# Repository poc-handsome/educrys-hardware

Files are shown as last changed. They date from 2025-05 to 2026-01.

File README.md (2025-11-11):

# educrys-hardware


Subfolders contain the documentation for [mechanical](/mechanical-design) (TODO) and [electronic](/electronic-design) (TODO) design of EduCrys setup for the users who want to build or adapt it by themselves.

The sections below provide information for users who have received a ready-to-use setup.

## Packing

While most electronic components of EduCrys are enclosed in a robust metallic box, many sensors and other parts need careful packing to avoid damage during transport. The pictures below show an example of such packing. The final package has dimensions of 60x41x23 cm and weight of 13.3 kg.

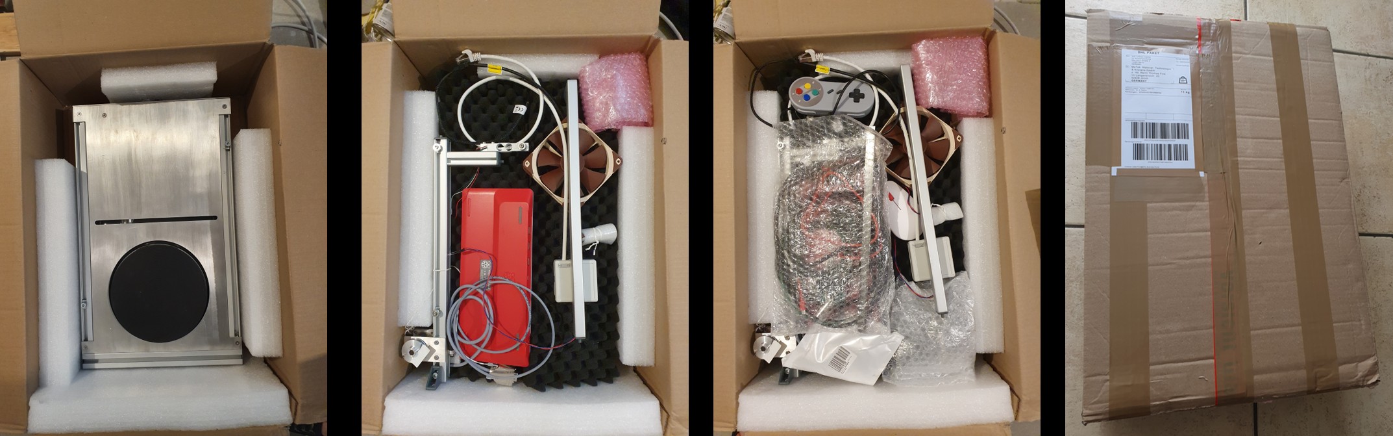
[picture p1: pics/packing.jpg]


## Transport without packing

If the EduCrys setup is transported in the partly-assembled state, the following safety measures are recommended:

- Disconnect the rotation motor, detach the seed holder, wind the pulling wire on the main pulley and fix it with a tape
- Disconnect the camera and detach it from the magic arm
- Tape the crucible and camera cable to the main body to prevent motion
- Pack the seed holder and camera separately

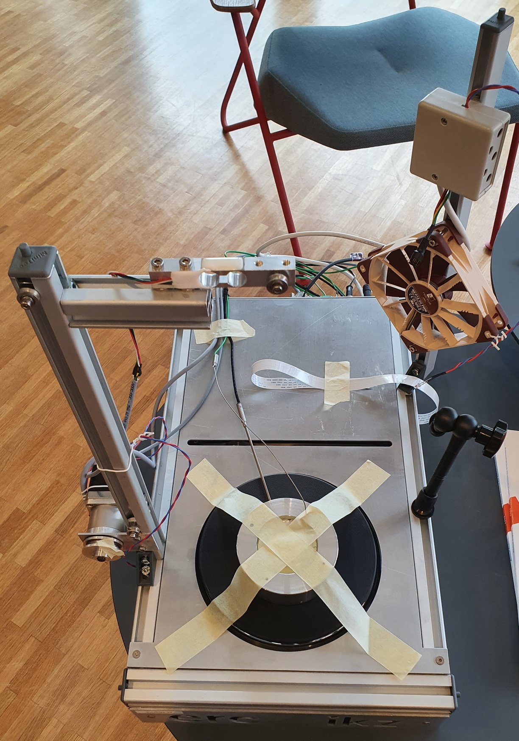
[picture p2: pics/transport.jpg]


## List of components

### Main components

- Main body with all connectors detached, except the camera cable, which is taped on the right wall. Two M6 screws are left in the profiles on both sides.
- Main stand with the pulling motor and weight cell. The pulling wire is wound and taped on the motor roll.
- Second stand with the fan and the small sensor box. The infrared sensor and LED should be protected with bubble wrap.
- Seed holder with a rotation motor in a bubble wrap bag. Small S-shaped hook to attach the seed holder to the pulling wire.
- Aluminum crucible with solid tin (99.9%), in a bubble wrap bag, should not move around in the transport box.

### Sensors and cables

- Raspberry Pi camera with a cover, attached to a magic arm, all inside a bubble wrap
- 1x PT100 and 2x thermocouple sensors with about 1.5 m wire length
- Raspberry Pi keyboard incl. USB cable and mouse, gamepad
- HDMI monitor cable, power cable

### Tools

- 30 cm metallic ruler
- Small spoon and small metal blow to be used when removing oxide layer
- 3 Inbus keys for seed holder, for opening main body, and for mounting both vertical profiles
- Nylon wire, which can be used temporarily if the steel wire of the seed holder breaks
- Warning sign for hot surfaces

### Raw material

- About 1 mm thick tin crystal, which can be used as seed
- About 1 mm thick copper wire, which can be used as seed
- (Tin pellets with 99.9% purity)

### Not included
- Protective glasses when working close to the crucible. **The hot liquid metal may splash if something falls into the melt!**
- Protective gloves when touching the hot crucible, for example, to adjust its position.
- Monitor
- Power strip

## Assembling the setup

### Mechanical

- Place the main body on a table with the logo on the front
- Attach the main stand on the left profile with a M6 screw, close to the front. Connect the motor and weight cell cables.
- Attach the fan stand on the right profile with a M6 screw, close to the back. Connect the fan and sensor cables.
- Guide the pulling wire over 3 pulleys from the pulling motor to the weight cell. Insert a hook in the loop at the wire end. Keep the wire tightened, otherwise it will unwind itself from the pulley on the motor axis.
- Hang the seed holder on the hook. The tilt of the seed holder should remain adjustable in two perpendicular directions.
- Attach the cable with two pins to the rotation motor. The polarity is not important. Keep the free length of this cable sufficient during the motion of the seed holder. This cable prevents the seed holder from rotating, but it should not pull it away from the vertical axis.
- Place the crucible on the hotplate. Check that the seed holder is in the middle of the crucible. Adjust the main stand position if necessary.

### Sensors and cables

- Attach the magic arm with camera on the right profile, close to the front. Carefully pull out the camera cable from the slit in the right wall. Insert the cable end into the connector at the back of the camera with the conducting pins towards the board. Push the black connector part upwards to fix the cable.
- Insert the PT100 sensor in a horizontal borehole and one thermocouple in a vertical borehole of the crucible. Both sensor cables should be bound together to prevent the PT100 sliding out of the hole. **This would lead to strong overheating of the crucible during temperature-controlled heating!**
- The second thermocouple could be used to measure ambient air, melt, or some parts inside the main body.
- Connect the keyboard with the red USB cable to the socket in the right wall. Connect the mouse and the gamepad to the keyboard. The USB ports in the keyboard can be also used to attach USB flash memory for data transfer.
- Connect a monitor to the HDMI socket in the right wall.
- Attach the power cable at the back of the main body. **Raspberry Pi starts as soon as power is connected! Always use the shutdown function in the Menu before disconnecting the power to avoid data loss.**
- If necessary, a network cable can be attached directly to the Raspberry Pi board through an opening in the back wall. Remove the screws and carefully pull the back wall for about 5 cm to access Raspberry Pi. **The network socket in the back wall can be only used for the sensor box.**

### Clock 

- Check the system clock after the log in. Newer EduCrys setups have a hardware clock with battery backup, while others rely on synchronization over network.
- The following steps are required to install an external hardware clock, see also [raspberry-pi-geek.de](https://www.raspberry-pi-geek.de/ausgaben/rpg/2015/03/echtzeituhr-modul-ds3231-sorgt-fuer-genaue-zeitangaben/2/) 
  - Update system time: `sudo date -s "19 May 2025 18:00:00" `
  - Attach the hardware clock to the I2C bus and find the address (e.g. 68): `sudo i2cdetect -y 1`
  - Configure the system to use the hardware clock (use the address from above) and add this line also to /etc/rc.local: `echo ds3231 0x68 | sudo tee /sys/class/i2c-adapter/i2c-1/new_device`
  - Synchronize the hardware clock with system time: `sudo hwclock -w`
  - Disable synchronization over network: `sudo update-rc.d ntp disable`   `sudo update-rc.d fake-hwclock disable`   `sudo timedatectl set-ntp false`

The final setup should look like this.



## Acknowledgements

[This project](https://poc-handsome.github.io/) has received funding from the European Research Council (ERC) under the 
European Union’s Horizon Europe framework programme for research and innovation (grant agreement No. 101122970).



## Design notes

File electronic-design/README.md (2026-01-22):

## E01 PCB

### Layout of the PCB

Design files for KiCad (8.0.0) are here: [KiCad](https://github.com/poc-handsome/educrys-hardware/tree/main/electronic-design/E01/KiCad)

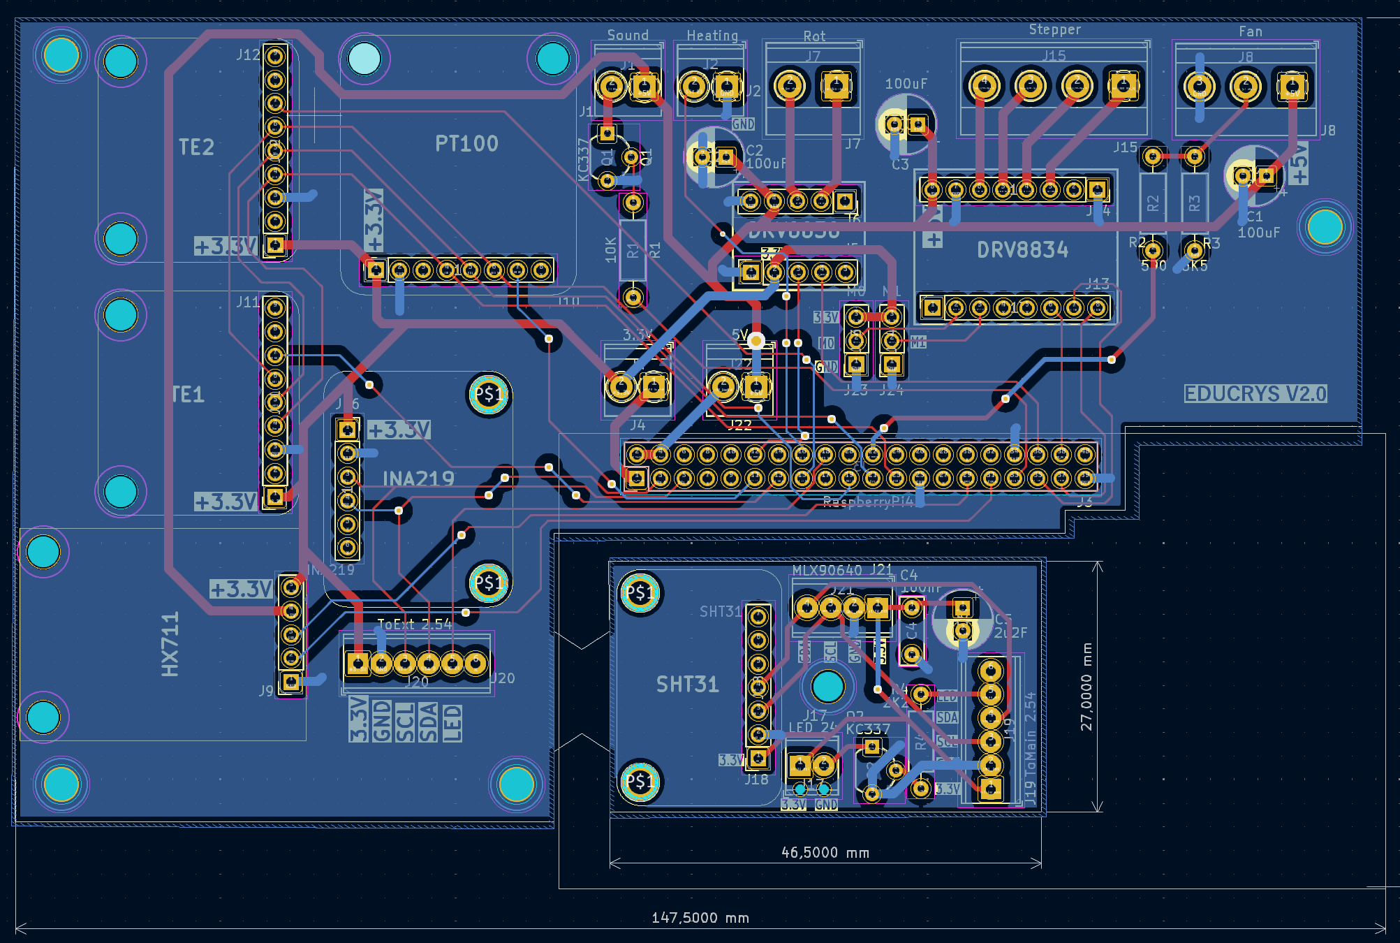
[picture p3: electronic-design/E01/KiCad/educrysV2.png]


The following improvements have not been implemented yet:
- Separate pin header for the clock module
- Larger screw terminal for the connection between main PCB and sensor PCB
- Avoid risk of short circuit when soldering capacitors

### Soldering

Main PCB with soldered parts, top and bottom views:

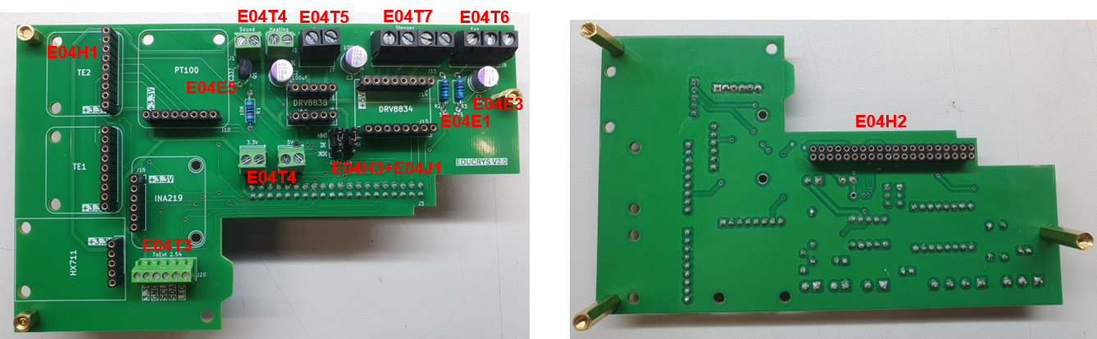
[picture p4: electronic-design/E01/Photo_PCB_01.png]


Sensor PCB with soldered parts, top and bottom views:

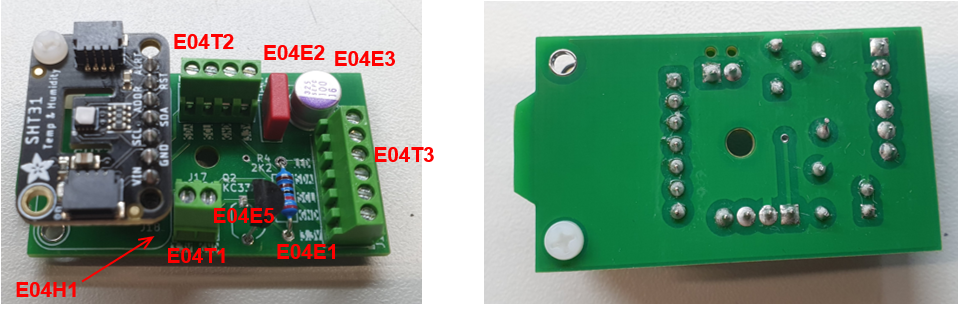
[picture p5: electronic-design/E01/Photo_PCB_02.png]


Remarks:
- The connection between the main board and sensor board must be cut 
- For all screw terminals the holes are oriented to the rim of the board 
- A small 2 mm gap should be left between the 100 uF capacitor to avoid short circuit 
- Resitor values are not printed correctly on the board, use closes E12 values
- All flux residues should be cleaned from both board sides, e.g. using Kontaktchemie LR

### Modules

PCB after mounting the modules:

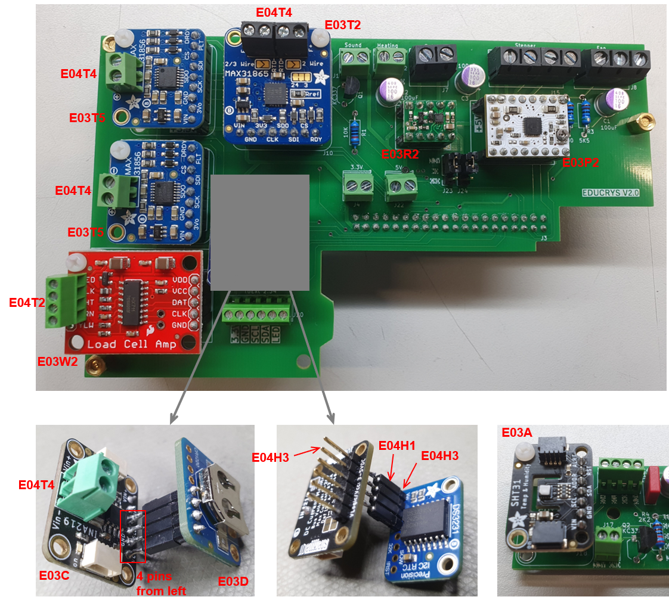
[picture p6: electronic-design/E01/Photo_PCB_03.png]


Remarks:

- First solder pin headers [E04H3] on the bottom of all modules [E03T2 etc.]. Make short breaks to avoid overheating the chip
- Solder screw terminals on the top of modules [E03T5, E03T2, E03W2, E03C]. The holes are oriented to the center of the board for [E03T5, E03W2] and to the rim of the board for [E03T2, E03C]
- Solder a female header on the top of the module [E03C] (4 pins on the left) and connect the module [E03D] there
- All flux residues should be cleaned from both board sides, e.g. using Kontaktchemie LR
- The modules will be fastened later to the PCB with a 10 mm spacer and two M2.5 screws. M3 screws are too big!

## E02 Wiring diagram

Schematic of the connections using the parts given below:

(pic)

Photo of the final wiring

(pic)

Remarks:

## E03 Devices: sensors, actuators

Prices are given per one piece in EUR incl. VAT. 

| Part  | Description                             | Use               | Price | Vendor/Link              | Datasheet | 
|-------|-----------------------------------------|-------------------|-------|--------------------------|-----------|
| E03H  | Hotplate, Severin KP 1092               | Crucible heating  | 27.99 | [Conrad/704233](https://www.conrad.de/de/p/severin-kp-1092-1092-kochplatte-704233.html?searchType=SearchRedirect)       |           |
| E03P1 | Stepper, Nema-17 1:20                   | Crystal pulling   | 56.90 | [Conrad/2355877](https://www.conrad.de/de/p/joy-it-schrittmotor-nema17-07gm-0-44-nm-1-68-a-wellen-durchmesser-8-mm-2355877.html?searchType=SearchRedirect)        |           |
| E03P2 | Motor driver IC, DRV8834                | Stepper motor     | 8.24  | [Exptech/80-2134](https://exp-tech.de/products/pololu-drv8834-low-voltage-stepper-motor-driver-carrier)     |           |
| E03R1 | DC motor 1000:1                         | Seed rotation     | 12.95 | [Conrad/1289388](https://www.conrad.de/de/p/sol-expert-g1000-micro-getriebemotor-g-1000-metallzahnraeder-1-1000-2-18-u-min-1289388.html?searchType=SearchRedirect)      |           |
| E03R2 | Motor driver IC, DRV8838                | DC motor          | 4.10  | [Exptech/80-2990](https://exp-tech.de/products/pololu-drv8838-single-brushed-dc-motor-driver-carrier)      |           |
| E03F1 | Fan, 120 mm, 5V                         | Crystal cooling   | 35.61 | [Conrad/816459971](https://www.conrad.de/de/p/noctua-nf-f12-5v-pwm-fan-1-pack-brun-120-mm5-v-pwm-0-75-w-0-15-a-93-4-816459971.html?searchType=SearchRedirect)    |           |
| E03W1 | Weight cell, 1 kg                       | Crystal weight    | 39.37 | [Conrad/2104290](https://www.conrad.de/de/p/sauter-ck-1-0p1-ck-1-0p1-messzelle-ck-p1-4-2104290.html?searchType=SearchRedirect)      |           |
| E03W2 | Weight cell driver IC, HX711            | Weight cell       | 9.86  | [Digikey/1568-1436-ND](https://www.digikey.de/de/products/detail/sparkfun-electronics/13879/6202732?s=N4IgTCBcDaIIwFYBsAOAtHALAZiWgcgCIgC6AvkA)     |           |
| E03T1 | Thermal sensor PT100, 3x150 mm, 500 °C  | Temperature sensor | 142.87 | [RS/397-1315](https://de.rs-online.com/web/p/widerstands-temperatursensoren/3971315?searchId=d1256e21-5988-4aaf-8b94-83c79a26ba8f)             |           |
| E03T2 | PT100 driver IC, MAX31865               | Temperature sensor | 12.82 | [Digikey/1528-3328-ND](https://www.digikey.de/de/products/detail/adafruit-industries-llc/3328/6562952)    |           |
| E03T4 | 2x Thermocouple, Type K, 1x250 mm, 750 °C | Temperature sensor | 47.36 | [RS/787-7706](https://de.rs-online.com/web/p/thermoelemente/7877706?searchId=9bbca203-3abb-4fba-a2c3-11345d2f288b)       |           |
| E03T5 | Thermocouple driver IC, MAX31856        | Temperature sensor | 17.98  | [Digikey/1528-1772-ND](https://www.digikey.de/de/products/detail/adafruit-industries-llc/3263/6227009?s=N4IgTCBcDaIIwFYwA4C0cDsGyoHIBEQBdAXyA)    |           |
| E03C  | Current sensor, INA219                  | Motor current     | 8.53   | [Digikey/1528-904-ND](https://www.digikey.de/de/products/detail/adafruit-industries-llc/904/5353628?s=N4IgTCBcDaIIwFYwA4C0BOADAFlQOQBEQBdAXyA)      |           |
| E03A  | Air sensor, SHT31                       | Air temperature, humidity | 11.96 | [Digikey/1528-2857-ND](https://www.digikey.de/de/products/detail/adafruit-industries-llc/2857/5804106?s=N4IgTCBcDaIIYBM4DMBOBXAlgFwAQGUAJAFQGYBGEAXQF8g) |           |
| E03I  | IR sensor, MLX90640                     | Hotplate temperature | 30.28 | [Digikey/MLX90640ESF-BAB-000-TU-ND](https://www.digikey.de/de/products/detail/melexis-technologies-nv/MLX90640ESF-BAB-000-TU/8638464?s=N4IgTCBcDaILIBkAaBOADANgCxoKIGUAxAWgCEBBU4tG4gFQFViA5AERAF0BfIA) |           |
| E03D  | Real time clock, DS3231                 | Raspberry Pi time backup | 15.0  | [Digikey/1528-3013-ND](https://www.digikey.de/de/products/detail/adafruit-industries-llc/3013/5875808) |           |
| E03O1 | RPi camera                              | Optical camera | 51.90 | [Welectron/RP3-102610](https://www.welectron.com/Offizielle-Raspberry-Pi-HQ-Camera)        |           |
| E03O2 | Camera lens 8-50 mm                     | Optical camera | 42.90 | [Welectron/WS9-018245](https://www.welectron.com/Waveshare-18245-8-50mm-Zoom-Lens-for-Pi)        |           |

## E04 Electrical components

Prices are given per one piece in EUR incl. VAT. In some cases SETS with a larger number of parts are given.

| Part  | Description                             | Use               | Price | Vendor/Link              | Datasheet | 
|-------|-----------------------------------------|-------------------|-------|--------------------------|-----------|
| E04S1 | 2x Power socket                         | SSR box           | 4.79  | [Conrad/2484787](https://www.conrad.de/de/p/as-schwabe-45084-einbau-steckdose-grau-2484787.html?searchType=SearchRedirect)  |  |
| E04S2 | Solid state relais                      | SSR box           | 74.52 | [RS/491-4947](https://de.rs-online.com/web/p/halbleiterrelais/4914947)  |  |
| E04R1 | Raspberry Pi 4 B (4 GB)                 |                   | 57.90 | [Welectron/RP1-141400](https://www.welectron.com/Raspberry-Pi-4-B-4-GB)  |  |
| E04R2 | SD card 64GB                            | Raspberry Pi      | 6.9   | [Welectron/SD1-200644](https://www.welectron.com/SanDisk-SDSQUAB-064G-GN6MA-Ultra-microSD-Speicherkarte-64-GB-140-MB-s)  |  |
| E04R3 | Heatsink                                | Raspberry Pi      | 1.3   | [Welectron/409151](https://www.welectron.com/Raspberry-Pi-Kuehlkoerpersatz)  |  |
| E04R4 | Power supply 5V, 3A                     | Raspberry Pi      | 7.5   | [Welectron/408024-012](https://www.welectron.com/Offizielles-Raspberry-Pi-4-Steckernetzteil-USB-C-51V-3A-weiss-EU)  |  |
| E04R5 | Keyboard + mouse                        | Raspberry Pi      | 27.90 | [Welectron/409483-002](https://www.welectron.com/Offizielle-Raspberry-Pi-Tastatur-Maus-Kombination-rot-weiss-DE)  |  |
| E04R6 | Gamepad                                 | Raspberry Pi      | 4.99  | [Conrad/1954771](https://www.conrad.de/de/p/joy-it-gamepad-snes-design-gamepad-raspberry-pi-universal-grau-1954771.html?searchType=SearchRedirect)  |  |
| E04E1 | SET: Metal film resistors               | PCB               | 46.65 | [Reichelt/METALL E 12](https://www.reichelt.de/de/de/shop/produkt/metallschichtwiderstandssortiment_e12-12049)  |  |
| E04E2 | SET: Foil capacitors                    | PCB               | 83.50 | [Reichelt/SORTIMENT 100](https://www.reichelt.de/de/de/shop/produkt/sortimentsbox_folienkondensatoren_rm_5mm-19263)  |  |
| E04E3 | 4x Capacitor 100 uF                     | PCB               | 1.29  | [Conrad/1179727](https://www.conrad.de/de/p/panasonic-16sepc100m-elektrolyt-kondensator-radial-bedrahtet-2-5-mm-100-f-16-v-dc-20-o-x-h-6-3-mm-x-6-mm-1-st-1179727.html)  |  |
| E04E4 | Buzzer                                  | PCB               | 0.99  | [Reichelt/KXG1205C](https://www.reichelt.de/de/de/shop/produkt/indikator_85db_2300_hz_5_v-360852)  |  |
| E04E5 | 2x Transistor KC337                     | PCB               | 0.02  | [Reichelt/BC 337-16](https://www.reichelt.de/de/de/shop/produkt/bipolartransistor_npn_45v_0_8a_0_625w_to-92-4985)  |  |
| E04E6 | White LED                               | Sensor box        | 0.5   | [Conrad/180754](https://www.conrad.de/de/p/nichia-nspw300ds-sel-b2v-w-led-bedrahtet-weiss-rund-3-mm-15000-mcd-20-20-ma-3-2-v-180754.html)  |  |
| E04H1 | 3x Female header precision, 2.54 mm, 1x36 | PCB             | 3.79  | [Conrad/733779-VQ](https://www.conrad.de/de/p/mpe-garry-buchsenleiste-praezision-anzahl-reihen-1-polzahl-je-reihe-36-115-1-036-0-mtf-xs0-1-1-st-733779.html)  |  | 
| E04H2 | 2x Female header precision, 2.54 mm, 2x10 | PCB             | 2.79  | [Conrad/733843-VQ](https://www.conrad.de/de/p/mpe-garry-buchsenleiste-praezision-anzahl-reihen-2-polzahl-je-reihe-10-115-3-020-0-mtf-xs0-1-st-733843.html)  |  |
| E04H3 | 2x Pin header, 2.54 mm, 1x50              | PCB             | 1.79  | [Conrad/734220-VQ](https://www.conrad.de/de/p/mpe-garry-stiftleiste-standard-anzahl-reihen-1-polzahl-je-reihe-50-087-1-050-0-s-xs0-1260-1-st-734220.html)  |  |
| E04T1 | Screw terminal, 2.54 mm, 2p               | PCB             | 0.34  | [Conrad/567588-83](https://www.conrad.de/de/p/ptr-hartmann-50692020021e-schraubklemmblock-0-75-mm-polzahl-2-gruen-1-st-567588.html)  |  |
| E04T2 | Screw terminal, 2.54 mm, 4p               | PCB             | 0.68  | [Conrad/567658-83](https://www.conrad.de/de/p/ptr-hartmann-50692040021e-schraubklemmblock-0-75-mm-polzahl-4-gruen-1-st-567658.html)  |  |
| E04T3 | 2x Screw terminal, 2.54 mm, 6p            | PCB             | 0.96  | [Conrad/567757-83](https://www.conrad.de/de/p/ptr-hartmann-50692060021e-schraubklemmblock-0-75-mm-polzahl-6-gruen-1-st-567757.html)  |  |
| E04T4 | 4x Screw terminal, 3.5 mm, 2p             | PCB             | 0.57  | [Conrad/732295-83](https://www.conrad.de/de/p/ptr-hartmann-50602020021f-schraubklemmblock-1-00-mm-polzahl-2-gruen-1-st-732295.html)  |  |
| E04T5 | Screw terminal, 5.08 mm, 2p               | PCB             | 0.19  | [Conrad/731877-83](https://www.conrad.de/de/p/ptr-hartmann-50500020134g-schraubklemmblock-1-50-mm-polzahl-2-grau-1-st-731877.html)  |  |
| E04T6 | Screw terminal, 5.08 mm, 3p               | PCB             | 0.29  | [Conrad/731891-83](https://www.conrad.de/de/p/ptr-hartmann-50500030134g-schraubklemmblock-1-50-mm-polzahl-3-grau-1-st-731891.html)  |  |
| E04T7 | Screw terminal, 5.08 mm, 4p               | PCB             | 0.39  | [Conrad/731908-83](https://www.conrad.de/de/p/ptr-hartmann-50500040134g-schraubklemmblock-1-50-mm-polzahl-4-grau-1-st-731908.html)  |  |
| E04J1 | 2x Jumper                                 | PCB             | 0.05  | [Reichelt/MPE 149-1-002-F0](https://www.reichelt.de/de/de/shop/produkt/jumper_2_54_mm_geoeffnet_schwarz-119941)  |  |

## E05 Connectors

Prices are given per one piece in EUR incl. VAT. 

| Part  | Description                             | Use               | Price | Vendor/Link              | Datasheet | 
|-------|-----------------------------------------|-------------------|-------|--------------------------|-----------|
| E05P1 | Power socket with fuse, 10A, C14        | Power cable       | 3.29  | [Conrad/2522092](https://www.conrad.de/de/p/tru-components-tc-10088368-kaltgeraete-steckverbinder-c14-stecker-einbau-vertikal-gesamtpolzahl-3-10-a-schwarz-1-st-2522092.html)           |           |
| E05P2 | Fuse (250V, 8A, Flink)                  | Power socken      | 0.18  | [Conrad/524207](https://www.conrad.de/de/p/eska-520-526-520526-feinsicherung-o-x-l-5-mm-x-20-mm-8-a-250-v-flink-f-inhalt-10-st-524207.html?searchType=SearchRedirect)        |           |
| E05M1 | Socket SUB-D-9                          | Motors            | 0.34  | [Conrad/1389963](https://www.conrad.de/de/p/connfly-ds1033-09fbnsiss-ct-d-sub-buchse-180-polzahl-9-loeten-1-st-1389963.html?searchType=SearchRedirect)           |           |
| E05M2 | Jack SUB-D-9                            | Motors            | 1.95  | [Reichelt/MHDTZK 9 S](https://www.reichelt.de/de/de/shop/produkt/d-sub_stecker_9_polig-342366)      |           |
| E05M3 | 2x SUB-D screws                         | Motors            | 0.63  | [Digikey/609-1421-ND](https://www.digikey.de/de/products/detail/amphenol-cs-fci/863001061TLF/1001735)      |           |
| E05T1 | 2x Socket, Type-K                       | Thermocouple      | 4.79  | [Conrad/121365-VQ](https://www.conrad.de/de/p/b-b-thermo-technik-0220-0005-miniaturdose-typ-k-gelb-50-120-c-gelb-inhalt-1-st-121365.html?searchType=SearchRedirect)            |           |
| E05T2 | 2x Jack, Type-K                         | Thermocouple      | 3.79  | [Conrad/133523-VQ](https://www.conrad.de/de/p/b-b-thermo-technik-0220-0001-miniaturstecker-typ-k-gelb-gelb-inhalt-1-st-133523.html?searchType=SearchRedirect)            |           |
| E05S1 | Socket, DIN-6                           | PT sensor         | 5.49  | [Conrad/733449-VQ](https://www.conrad.de/de/p/lumberg-0103-06-din-rundsteckverbinder-flanschbuchse-kontakte-gerade-polzahl-6-silber-1-st-733449.html?searchType=SearchRedirect)            |           |
| E05S2 | Jack, DIN-6                             | PT sensor         | 5.99  | [Conrad/733336](https://www.conrad.de/de/p/lumberg-0131-06-din-rundsteckverbinder-stecker-gerade-polzahl-6-silber-1-st-733336.html?searchType=SearchRedirect)            |           |
| E05W1 | Socket, M8, 09-3390-80-04               | Weight cell       | 12.90 | [Conrad/733875](https://www.conrad.de/de/p/binder-09-3390-80-04-sensor-aktor-einbausteckverbinder-m8-buchse-gerade-polzahl-sensoren-4-1-st-733875.html?searchType=SearchRedirect)            |           |
| E05W2 | Jack, M8, 99-3383-00-04                 | Weight cell       | 13.99 | [Conard/746035](https://www.conrad.de/de/p/binder-99-3383-00-04-sensor-aktor-steckverbinder-unkonfektioniert-m8-stecker-gerade-polzahl-sensoren-4-1-st-746035.html?searchType=SearchRedirect)            |           |
| E05N1 | Socket, RJ45                            | Sensor box        | 5.99  | [Conrad/1497957](https://www.conrad.de/de/p/tru-components-rj-45-einbaubuchse-93038c234-1-st-1497957.html?searchType=SearchRedirect)           |           |
| E05H  | Feedthrough HDMI                        | Monitor	          | 9.75  | [Conrad/2473497](https://www.conrad.de/de/p/fm-slim-ft-hdmi-f-f-3-2-hole-adapter-einbau-cp30600gx1-cliff-inhalt-1-st-2473497.html?searchType=SearchRedirect)           |           |
| E05U  | Feedthrough USB                         | Keyboard          | 7.49  | [Conrad/2354829](https://www.conrad.de/de/p/adapter-buchse-einbau-usb-buchse-typ-a-usb-buchse-typ-b-cp30609n-cliff-inhalt-1-st-2354829.html?searchType=SearchRedirect)           |           |

## E06 Cables

Prices are given per one piece in EUR incl. VAT. 

| Part  | Description                             | Use               | Price | Vendor/Link              | Datasheet | 
|-------|-----------------------------------------|-------------------|-------|--------------------------|-----------|
| E06P	| Power cable C13, 10A / plug,	1.5 m     | C14 power socket  | 3.49  | [Conrad/2521347](https://www.conrad.de/de/p/sygonix-sy-5042694-kaltgeraete-anschlusskabel-schwarz-1-50-m-2521347.html?searchType=SearchRedirect)           |           |
| E06U2	| USB Kabel	Type-A / Micro-B, 1 m         | Wall to keyboard  | 1.9   | [Welectron/RP9-205570](https://www.welectron.com/Offizielles-Raspberry-Pi-micro-USB-Kabel)     |           |
| E06C	| RPi camera cable, 0.5 m                 | RPi to camera     | 2.9   | [Welectron/GM7-210500](https://www.welectron.com/Groundmicro-FPC-Kabel-100mm-Pitch-15-Pin-fuer-Raspberry-Pi-CSI-DSI-50-cm)     |           |
| E06H	| HDMI cable Type-A / Micro-D, 0.5 m      | RPi to wall       | 1.9   | [Welectron/GB1-053780](https://www.welectron.com/Goobay-53780-micro-HDMI-Kabel-HDMI-20-050m)     |           |
| E06U1	| USB cable Type-A / Type-B 90 deg, 0.5 m | RPi to wall       | 1.39  |	[Welectron/GB1-093016](https://www.welectron.com/Goobay-93016-USB-B-Kabel-gewinkelt-USB-20-050m)     |           |

## E07 Wiring

### Order list 

Prices are given in EUR incl. VAT. Typically a higher amount of materials is given than needed for 1 device.

| Nr | Description                      | Amount | Price | Vendor/Link              | Datasheet | 
|----|----------------------------------|--------|-------|--------------------------|-----------|
| 10 | Brown wire, 1.5 mm2              | 10 m   | 4.5   | [Reichelt/H07VK 1,5-10BR](https://www.reichelt.de/de/de/shop/produkt/schaltlitze_h07v-k_1_5_mm_10_m_braun-69505)  |           |
| 11 | Blue wire, 1.5 mm2               | 10 m   | 4.5   | [Reichelt/H07VK 1,5-10BL](https://www.reichelt.de/de/de/shop/produkt/schaltlitze_h07v-k_1_5_mm_10_m_blau-69504)  |           |
| 12 | Green-yellow wire, 1.5 mm2       | 10 m   | 4.5   | [Reichelt/H07VK 1,5-10GG](https://www.reichelt.de/de/de/shop/produkt/schaltlitze_h07v-k_1_5_mm_10_m_gruen_gelb-69506)  |           |
| 13 | Wire set, 0.25 mm2               | 1      | 27.99 | [Conrad/2201407](https://www.conrad.de/de/p/quadrios-19011ca085-litze-lify-1-x-0-25-mm-blau-braun-grau-rot-schwarz-weiss-gelb-gruen-70-m-2201407.html?searchType=SearchRedirect)           |           |
| 14 | Cable, 6 x 0.25 mm2              | 5 m    | 19.95 | [Conrad/486478](https://www.conrad.de/de/p/kabeltronik-liyy-steuerleitung-6-x-0-25-mm-grau-10602500-meterware-486478.html?searchType=SearchRedirect)            |           |
| 15 | Cable, 4 x 0.14 mm2              | 25 m   | 17.40 | [Reichelt/LIYCY 04-25](https://www.reichelt.de/de/de/shop/produkt/steuerleitung_4x0_14mm_geschirmt_25m-ring-10302)     |           |
| 16 | Compensation wire, 4 x 0.14 mm2  | 5 m    | 17.45 | [Conrad/121329](https://www.conrad.de/de/p/b-b-thermo-technik-ausgleichsleitung-0230-0191-messbereich-temperatur-10-bis-105-c-121329.html?searchType=SearchRedirect)            |           |
| 17 | Network cable                    | 5      | 4.95  | [Conrad/2521890](https://www.conrad.de/de/p/renkforce-rf-5043780-rj45-netzwerkkabel-patchkabel-cat-5e-u-utp-2-00-m-weiss-mit-rastnasenschutz-1-st-2521890.html?searchType=SearchRedirect)           |           |
| 18 | Fan extenstion cable             | 3      | 16.47 | [Conrad/976188](https://www.conrad.de/de/p/pc-luefter-verlaengerungskabel-1x-pc-luefter-stecker-4pol-1x-pc-luefter-buchse-4pol-0-30-m-schwarz-akasa-976188.html?searchType=SearchRedirect)           |           |
| 19 | Wire set, 0.34 mm2               | 1      | 49.95 | [Eckstein/SF11367](https://eckstein-shop.de/SparkFunHook-UpWire-AssortmentSolidCore2C22AWG)         |           |
| 20 | Blank ferrule set                | 1      | 8.99  | [Conrad/2870591](https://www.conrad.de/de/p/quadrios-22c485-aderendhuelsen-sortiment-unisoliert-1000-st-2870591.html?searchType=SearchRedirect)           |           |
| 21 | Receptable, 4.75 mm              | 10     | 1.9   | [Reichelt/FSH-M1 4.75](https://www.reichelt.de/de/de/shop/produkt/flachsteckhuelse_nicht_isoliert_breite_4_75mm-24854)     |           |
| 22 | Insulation sleeve (from set)     | 1      | 9.1   | [Reichelt/QUAD 1908C181](https://www.reichelt.de/de/de/shop/produkt/flachstecker-huelsen_set_0_5_x_4_8_mm_0_5_-1_5_mm_100-teilig-280155)   |           |
| 23 | Ring cable lug, M6               | 10     | 0.8   | [Reichelt/RK-B-6](https://www.reichelt.de/de/de/shop/produkt/ring-kerbschuhe_fuer_m6_blau-15254)          |           |
| 24 | Ring cable lug, M4               | 10     | 1.3   | [Reichelt/VT RK-B-4](https://www.reichelt.de/de/de/shop/produkt/ring-kerbschuhe_fuer_m4_blau-231385)       |           |
| 25 | Insulated ferrule set            | 3      | 14.97 | [Conrad/2870580](https://www.conrad.de/de/p/quadrios-2010c392-aderendhuelsen-sortiment-teilisoliert-200-st-2870580.html?searchType=SearchRedirect)           |           |
| 26 | Heat shrink tube set             | 1      | 23.99 | [Conrad/2583933](https://www.conrad.de/de/p/quadrios-1807ca006-schrumpfschlauchsortiment-schwarz-schrumpfrate-3-1-1-set-2583933.html?searchType=SearchRedirect)           |           |

**Sum = 211.31 EUR**

### Parts

These must be built using the items (Nr) from the order list.

| Part  | Description            | Amount | Wire                        | Length      | Ends                                                 |
|-------|------------------------|--------|-----------------------------|-------------|------------------------------------------------------|
| E07S1 | SSR box/phase          | 2      | 10: brown, 1.5 mm2          | 75 mm       | 20: blank ferrule / 20: blank ferrule                |
| E07S2 | SSR box/neutral        | 1      | 11: blue, 1.5 mm2           | 200 mm      | 20: blank ferrule / 20: blank ferrule                |
| E07S3 | SSR box/ground         | 1      | 12: green-yellow, 1.5 mm2   | 150 mm      | 20: blank ferrule / 20: blank ferrule                |
| E07S4 | SSR box/supply/phase   | 1      | 10: brown, 1.5 mm2          | 250 mm      | 20: blank ferrule / 21: receptacle + 22: sleeve      |
| E07S5 | SSR box/supply/neutral | 1      | 11: blue, 1.5 mm2           | 250 mm      | 20: blank ferrule / 21: receptacle + 22: sleeve      |
| E07S6 | SSR box/supply/ground  | 1      | 12: green-yellow, 1.5 mm2   | 250 mm      | 20: blank ferrule / 23: cable lug                    |
| E07S7 | supply/ground/top      | 1      | 12: green-yellow, 1.5 mm2   | 250 mm      | 23: cable lug / 24: cable lug                        |
| E07S8 | supply/ground/back     | 1      | 12: green-yellow, 1.5 mm2   | 150 mm      | 23: cable lug / 21: receptacle + 22: sleeve          |
| E07S9 | SSR box/signal         | 1      | 13: brown+grey, 0.25 mm2    | 210 mm      | 25: isolated ferrule / 25: isolated ferrule          |

| Part  | Description            | Amount | Wire                        | Length      | Ends                                                 |
|-------|------------------------|--------|-----------------------------|-------------|------------------------------------------------------|
| E07M1 | Motors/inside          | 1      | 14: 6 x 0.25 mm2, no shield | 200 mm      | solder + 26: heat shrink tube / 25: isolated ferrule |
| E07M2 | Motors/outside         | 1      | 14: 6 x 0.25 mm2            | 800 mm      | solder / solder + 26: heat shrink tube               |
| E07M3 | Motor/DC               | 1      | XX: 2 x 0.14 mm2            | 800 mm      | solder + 26: heat shrink tube / ..                   |
| E07P1 | PT/inside              | 1      | 15: 4 x 0.14 mm2, no shield | 280 mm      | solder + 26: heat shrink tube / 25: isolated ferrule |
| E07T1 | TC/inside              | 2      | 16: 2 x 0.14 mm2            | 300 mm      | none / 25: isolated ferrule                          |
| E07W1 | Weight/inside          | 1      | 15: 4 x 0.14 mm2, no shield | 300 mm      | solder + 26: heat shrink tube / 25: isolated ferrule |
| E07W2 | Weight/outside         | 1      | 15: 4 x 0.14 mm2            | 1100 mm     | solder / solder + 26: heat shrink tube               |
| E07B1 | Sensor box/inside      | 1      | 17: 8 x 0.14 mm2, no shield | 280 mm      | solder + 26: heat shrink tube / 25: isolated ferrule |
| E07B2 | Sensor box/outside     | 1      | 17: 8 x 0.14 mm2            | 900 mm      | none / 25: isolated ferrule                          |
| E07F1 | Fan/inside             | 1      | 18: 3 x 0.14 mm2            | 150 mm      | none / 25: isolated ferrule                          |
| E07Z1 | Zummer/inside          | 1      | 19: 2 x 0.34 mm2, solid     | 50 mm       | none / solder + 26: heat shrink tube                 |
| E07I2 | IR sensor/outside      | 1      | 19: 4 x 0.34 mm2, solid     | 100 mm      | none / solder + 26: heat shrink tube                 |
| E07L2 | LED/outside            | 1      | 19: 2 x 0.34 mm2, solid     | 400 mm      | none / solder + 26: heat shrink tube                 |
| E07R1 | RPi/5V                 | 1      | 19: 2 x 0.34 mm2, solid     | 45 mm       | none / none                                          |
| E07R2 | RPi/3.3V               | 1      | 19: 1 x 0.34 mm2, solid     | 30 mm       | none / none                                          |

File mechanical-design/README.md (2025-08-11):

TODO: Add images with overview of 3D CAD

TODO: Add images for 3D CAD models and CAD drawings of all mechanical parts below

TODO: Add all CAD data in separate subfolders (Mxxx as name)

TODO: Add editable lists

## M01 Base plate

## M02 Top plate

## M03 Front plate

## M04 Back plate

## M05 Side plate left

## M06 Side plate right

## M07 Separating plate

## M08 Pulling motor: a) mount plate, b) pulley

## M09 Seed motor: a) holder, b) seed mount

## M10 SSR box: a) bottom, b) top

## M11 Sensor box: a) bottom, b) top, c) wall

## M12 Camera mount nut

## M13 Crucible

## M14 MiniTec profiles
Editable list: position, type, length, vendor link

## M15 MiniTec parts
Editable list: position, type, #, vendor link

## M16 Screws
Editable list: position, type, #, vendor link ([Würth](https://www.wuerth.de))

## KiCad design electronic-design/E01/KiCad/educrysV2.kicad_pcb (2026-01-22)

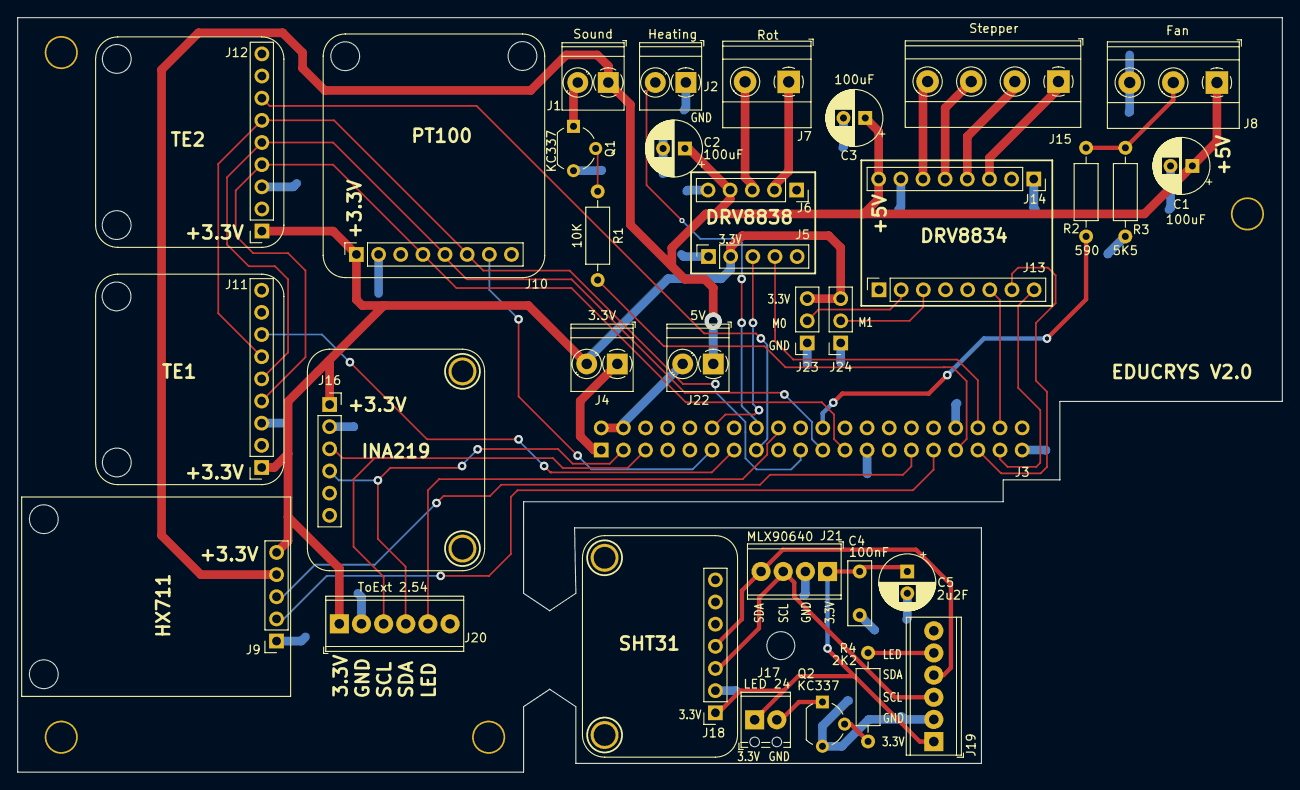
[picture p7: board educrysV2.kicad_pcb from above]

Board: 2 copper layers, 145.0 x 86.5 mm, 52 parts (1 on the bottom side), 42 nets.

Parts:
C1, C2, C3: 100uF; CP_Radial_D6.3mm_P2.50mm
C4: 100nF; C_Rect_L7.2mm_W2.5mm_P5.00mm_FKS2_FKP2_MKS2_MKP2
C5: 2u2F; CP_Radial_D6.3mm_P2.50mm
H1, H2, H3, H4, H5: MountingHole; MountingHole_3.2mm_M3_DIN965
J1: Sound; TerminalBlock_Phoenix_PT-1,5-2-3.5-H_1x02_P3.50mm_Horizontal
J2: Heating; TerminalBlock_Phoenix_PT-1,5-2-3.5-H_1x02_P3.50mm_Horizontal
J3: RaspberryPi4B; PinSocket_2x20_P2.54mm_Vertical
J4: 3.3V; TerminalBlock_Phoenix_PT-1,5-2-3.5-H_1x02_P3.50mm_Horizontal
J5: DRV8838_Left; PinSocket_1x05_P2.54mm_Vertical
J6: DRV8838_Right; PinSocket_1x05_P2.54mm_Vertical
J7: Rot; TerminalBlock_Phoenix_MKDS-1,5-2_1x02_P5.00mm_Horizontal
J8: Fan; TerminalBlock_Phoenix_MKDS-1,5-3_1x03_P5.00mm_Horizontal
J9: HX711; PinSocket_1x05_P2.54mm_Vertical
J10: PT100; PinSocket_1x08_P2.54mm_Vertical
J11: TE1; PinSocket_1x09_P2.54mm_Vertical
J12: TE2; PinSocket_1x09_P2.54mm_Vertical
J13: DRV8434_Left; PinSocket_1x08_P2.54mm_Vertical
J14: DRV8434_Right; PinSocket_1x08_P2.54mm_Vertical
J15: Stepper; TerminalBlock_Phoenix_MKDS-1,5-4_1x04_P5.00mm_Horizontal
J16: INA219; PinSocket_1x06_P2.54mm_Vertical
J17: LED 24; TerminalBlock_Phoenix_MPT-0,5-2-2.54_1x02_P2.54mm_Horizontal
J18: SHT31; PinSocket_1x07_P2.54mm_Vertical
J19: ToMain 2.54; TerminalBlock_Phoenix_MPT-0,5-6-2.54_1x06_P2.54mm_Horizontal
J20: ToExt 2.54; TerminalBlock_Phoenix_MPT-0,5-6-2.54_1x06_P2.54mm_Horizontal
J21: MLX90640; TerminalBlock_Phoenix_MPT-0,5-4-2.54_1x04_P2.54mm_Horizontal
J22: 5V; TerminalBlock_Phoenix_PT-1,5-2-3.5-H_1x02_P3.50mm_Horizontal
J23: M0; PinSocket_1x03_P2.54mm_Vertical
J24: M1; PinSocket_1x03_P2.54mm_Vertical
Q1, Q2: KC337; TO-92_Wide
R1: 10K; R_Axial_DIN0207_L6.3mm_D2.5mm_P10.16mm_Horizontal
R2: 590; R_Axial_DIN0207_L6.3mm_D2.5mm_P10.16mm_Horizontal
R3: 5K5; R_Axial_DIN0207_L6.3mm_D2.5mm_P10.16mm_Horizontal
R4: 2K2; R_Axial_DIN0207_L6.3mm_D2.5mm_P10.16mm_Horizontal
STANDOFF1, STANDOFF3, STANDOFF3#2, STANDOFF3#3, STANDOFF3#4, STANDOFF3#5, STANDOFF3#6, STANDOFF3#7: STAND-OFF
U$19, U$20, U$20#2, U$21: MOUNTINGHOLE2.5; MOUNTINGHOLE_2.5_PLATED

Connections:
+3.3V: J4.2, J5.2, J9.5, J10.1, J11.1, J12.1, J16.1, J20.1, J23.3, J24.3
+3.3V_EXT: C4.1, C5.1, J17.1, J18.1, J19.1, J21.1
+3.3V_LowEnd: J3.1, J4.1
+5V: C1.1, C2.1, C3.1, J1.1, J6.4, J8.1, J9.4, J14.8, J22.1
+5V_LowEnd: J3.2, J3.4, J22.2
FAN_PWM 25: J3.22, R2.2
GND: C1.2, C2.2, C3.2, J2.1, J3.25, J3.34, J3.39, J5.1, J6.5, J8.3, J9.1, J10.2, J11.3, J12.3, J14.1, J14.7, J16.2, J20.2, J23.1, J24.1, Q1.3 (E), R3.1
GND_EXT: C4.2, C5.2, J18.2, J19.2, J21.2, Q2.3 (E)
LED 24: J3.18, J20.5
LED 24_EXT: J19.5, R4.1
LIN_DIR 16: J3.37, J13.8
LIN_ON 20: J3.38, J13.6
LIN_PWM 19: J3.35, J13.7
unnamed: J1.2, Q1.1 (C)
unnamed: J6.2, J7.1
unnamed: J6.3, J7.2
unnamed: J8.2, R2.1, R3.2
unnamed: J13.2, J23.2
unnamed: J13.3, J24.2
unnamed: J14.3, J15.1
unnamed: J14.4, J15.2
unnamed: J14.5, J15.3
unnamed: J14.6, J15.4
unnamed: J17.2, Q2.1 (C)
unnamed: Q1.2 (B), R1.1
unnamed: Q2.2 (B), R4.2
PT100_CS 17: J3.11, J10.7
ROT_DIR 16: J3.36, J5.4
ROT_PWM 18: J3.12, J5.3
SCL 3: J3.5, J16.3, J20.3
SCL 3_EXT: J18.3, J19.3, J21.3
SDA 2: J3.3, J16.4, J20.4
SDA 2_EXT: J18.4, J19.4, J21.4
SOUND 13: J3.33, R1.2
SSR 23: J2.2, J3.16
TE1_CS 27: J3.13, J11.7
TE2_CS 22: J3.15, J12.7
T_CLK 11: J3.23, J10.4, J11.4, J12.4
T_SDI 9: J3.21, J10.5, J11.5, J12.5
T_SDI 10: J3.19, J10.6, J11.6, J12.6
W_CLK 6: J3.31, J9.2
W_DAT 5: J3.29, J9.3

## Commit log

2025-10-20 Revert "Uploaded files"
    [1593K BOTTOM.stp.STEP, 1593K Top.stp.STEP, 1593K-L-P-Q-X-Y Flat endplate.stp.STEP, 1599EBAT Box.stp.STEP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]
2025-10-20 Update wiring
2026-01-22 Update electronic documentation
    [educrysV2.kicad_pcb]
